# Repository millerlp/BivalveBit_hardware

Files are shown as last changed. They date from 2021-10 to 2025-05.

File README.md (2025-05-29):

# BivalveBit hardware
 Heart rate and valve gape sensor wearable for oysters and mussels. 
 This hardware is described in the publication "Monitoring bivalve behavior and physiology in the laboratory and field using open-source tools" L.P. Miller (2022) *Integrative and Comparative Biology*
 
 [https://doi.org/10.1093/icb/icac046](https://doi.org/10.1093/icb/icac046)
 
 * Based around a ATmega4808 microcontroller
 * Designed to fit inside a nominal 3/4" schedule 40 PVC plumbing pipe (<18.5mm
 inside diameter) along with an 18650 size Lithium-Ion battery cell. 
 * Provides one I2C 4-pin port for communicating with a IR heart rate sensor
 * Provides one analog 4-pin port for communicating with an analog sensor such
 as the A1395 Hall effect sensor (with SLEEP pin on the 4th wire). 
 * Writes data to a standard microSD card

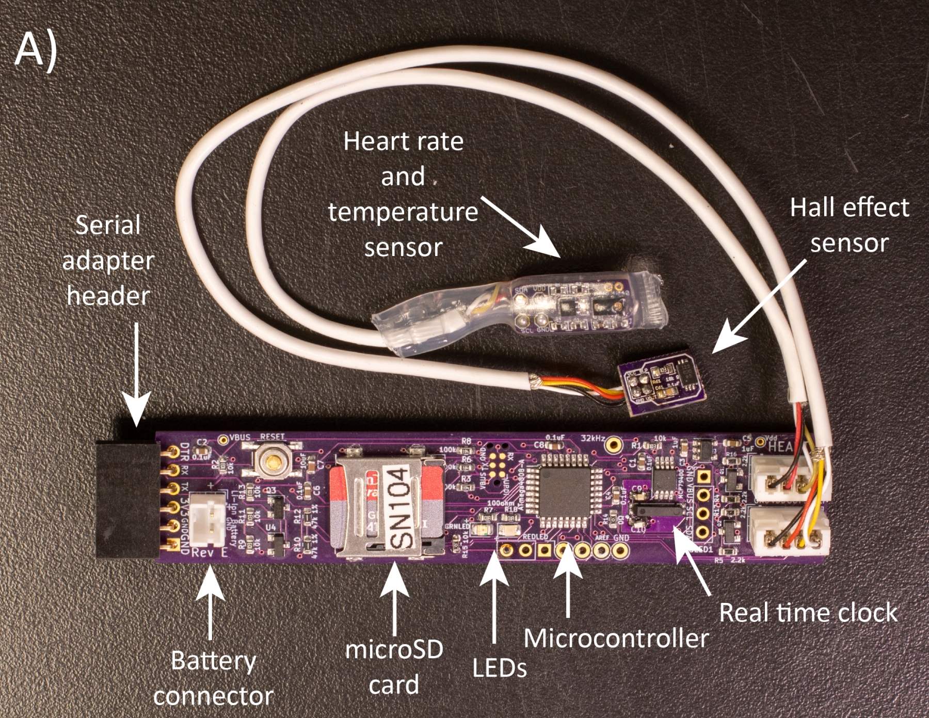
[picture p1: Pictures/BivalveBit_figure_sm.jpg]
Labeled image of the circuit board
 

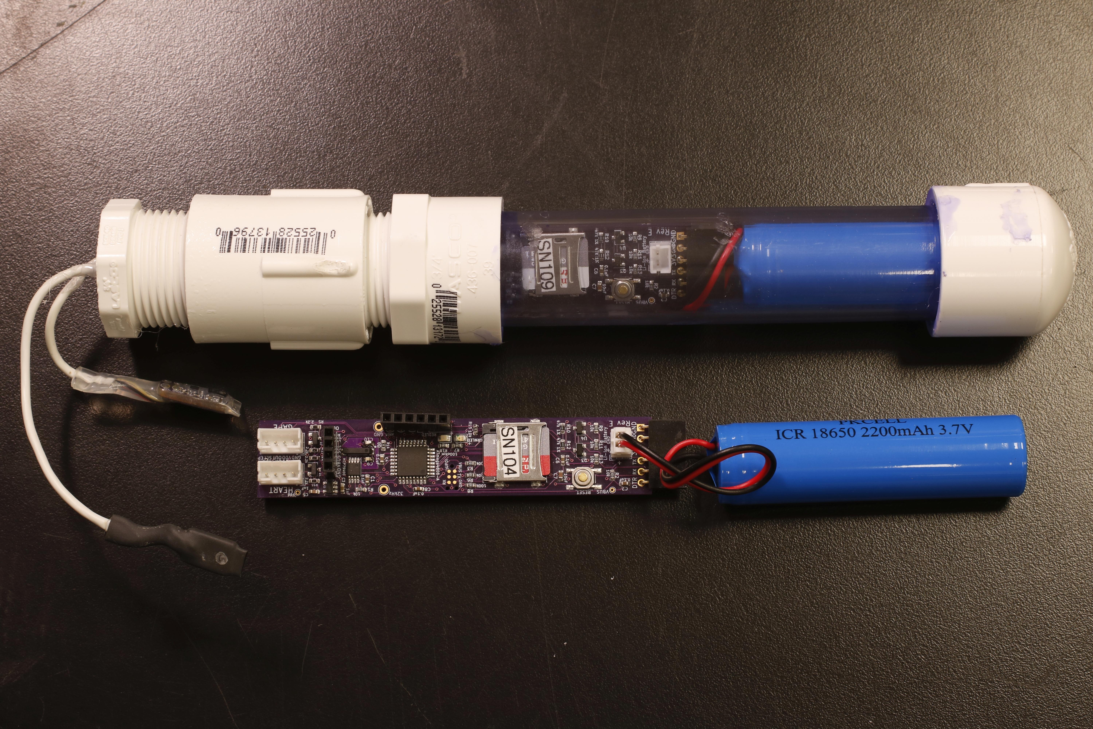
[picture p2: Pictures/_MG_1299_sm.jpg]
Data logger next to a PVC pipe housing


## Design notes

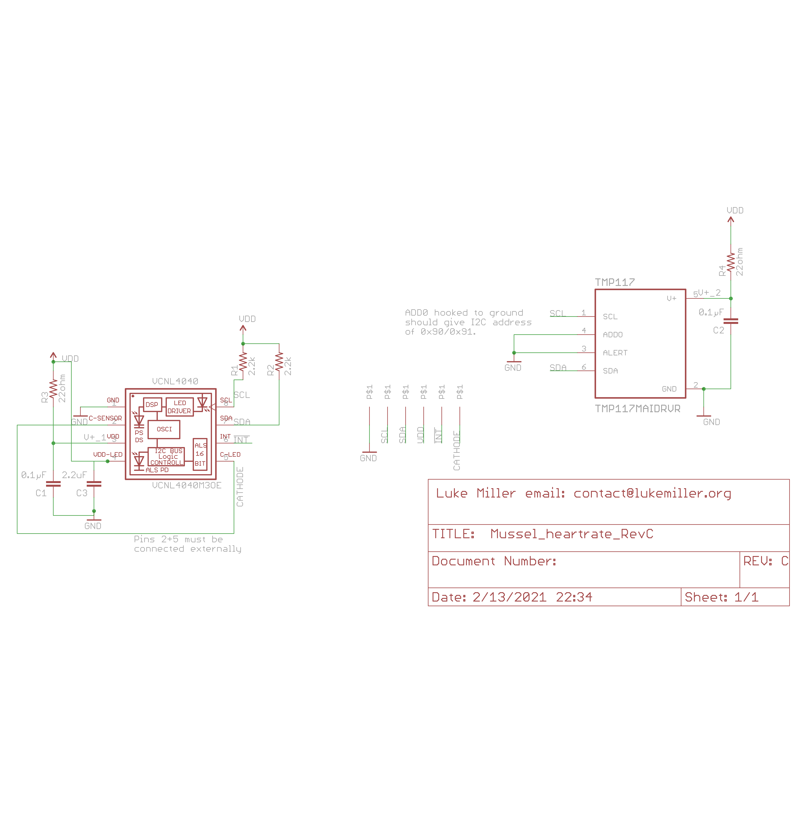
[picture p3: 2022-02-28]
Hardware/Mussel_heartrate_RevC_EAGLE/Mussel_heartrate_RevC_schematic.png

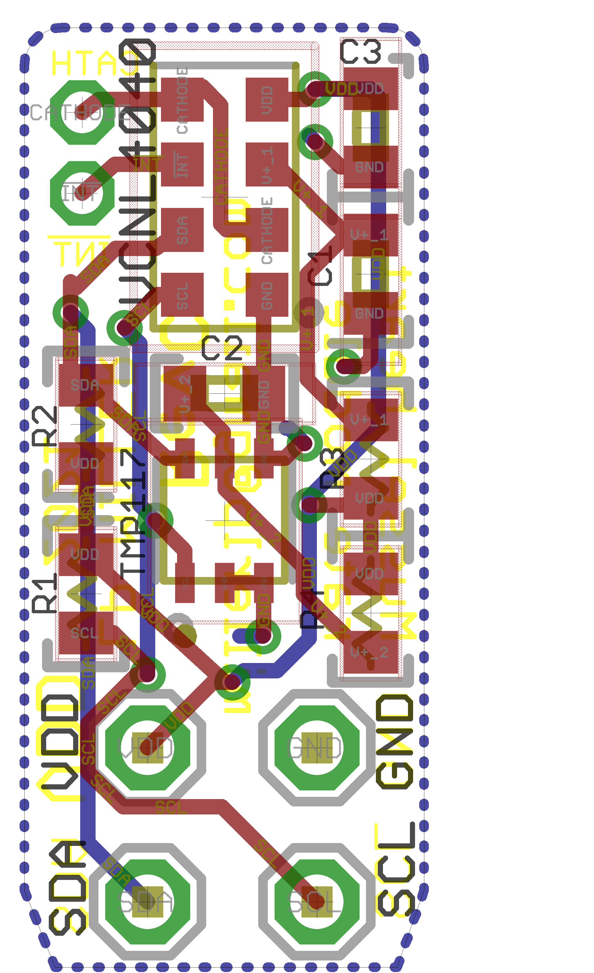
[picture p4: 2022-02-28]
Hardware/Mussel_heartrate_RevC_EAGLE/Mussel_heartrate_RevC_board.png

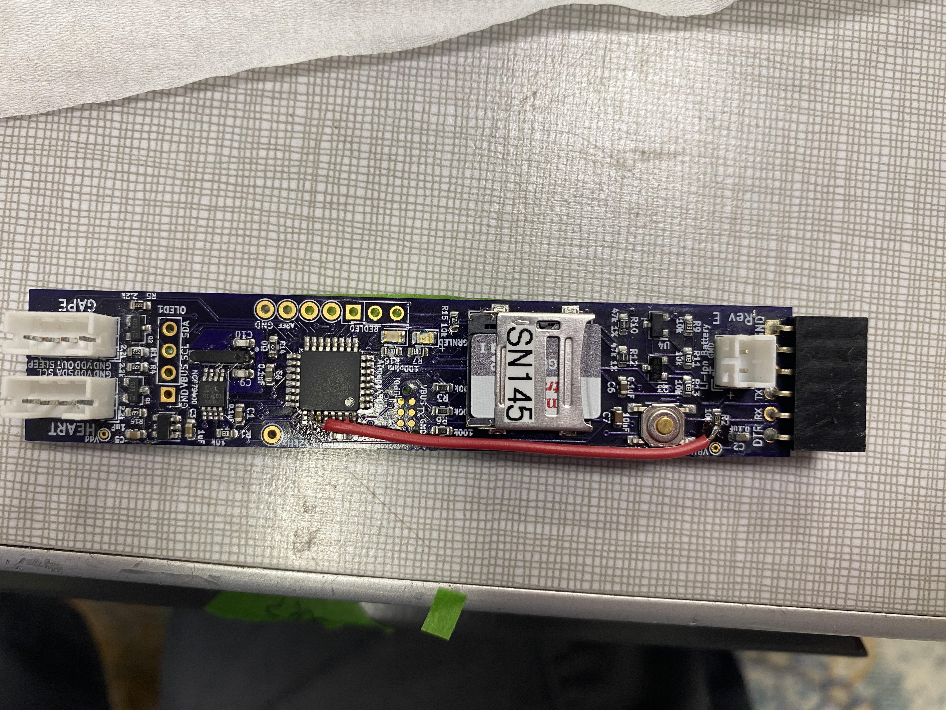
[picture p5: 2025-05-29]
Pictures/2023-08-01 10.56.35.jpg

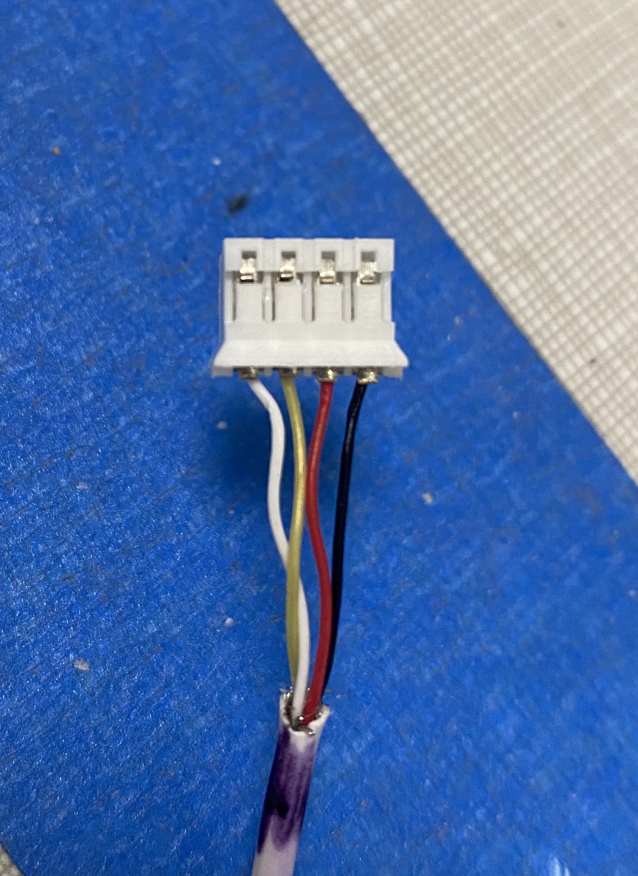
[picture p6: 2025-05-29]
Pictures/2021-09-30 13.38.30.jpg

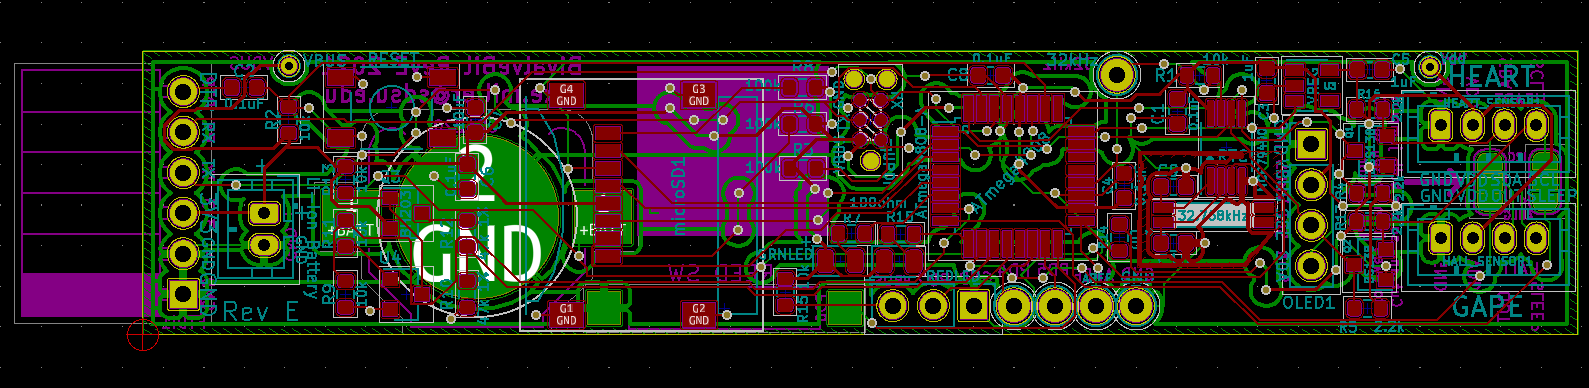
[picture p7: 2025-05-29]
Pictures/BivalveBit_layout_cropped.png

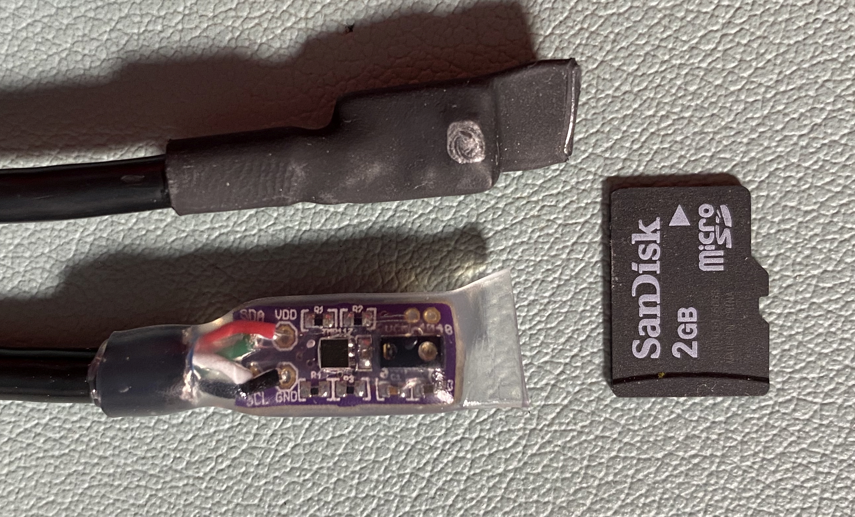
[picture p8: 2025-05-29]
Pictures/Sensors_closeup.jpg

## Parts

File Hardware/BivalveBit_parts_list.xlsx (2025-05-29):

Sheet: RevCDEF
BivalveBit RevC, RevD, RevE, RevF
Part Description | Manufacturer | Mfr. PN | Digikey PN | Quantity | Digikey $ | Extended $ | Alt. Mfr PN | Alt. Digikey PN | Digikey $
ATmega4808 32-pin TQFP package | Microchip | ATMEGA4808-AUR | 150-ATMEGA4808-AURCT-ND | 1 | $1.32 | $1.32
MCP79400 real time clock 8-MSOP | Microchip | MCP79400T-I/MS | MCP79400T-I/MSCT-ND | 1 | $0.90 | $0.90 | MCP7940NT-I/MS | MCP7940NT-I/MSCT-ND | $0.97
32.768kHz crystal 9pF ±10ppm for PCF8523 RTC | Seiko | SSPT7F-9PF10-R | 728-SSPT7F-9PF10-RCT-ND | 1 | $0.72 | $0.72
Capacitor - Crystal load 16pF ceramic 0603 1% tolerance | AVX Corp | 06035A160FAT2A | 478-06035A160FAT2ACT-ND | 2 | $0.27 | $0.54
Voltage regulator - LP5907QMFX 3.0V | Texas Inst. | LP5907QMFX-3.0Q1 | 296-40364-1-ND | 1 | $0.61 | $0.61
N-channel MOSFET - I2C level shifting, Q1,Q2 (BS138 or DMG2302U-7, Toshiba SSM3K329R,LF) | ON Semi. | BSS138 | BSS138CT-ND | 2 | $0.26 | $0.52 | DMG2302U-7 | DMG2302U-7DICT-ND | $0.40
Reed switch (optional, not used in 2022 builds) | Coto | CT10-2540-G1 | 306-1126-1-ND | 1 | $0.85 | $0.85
Capacitor 0.1uF - 0603 ceramic 25V | taiyo yuden | TMK107BJ104KA-T | 587-1245-1-ND | 5 | $0.10 | $0.50
Capacitor 1uF - 0603 ceramic X7R - for vreg | Samsung | CL10A105KB8NNNC | 1276-1860-1-ND | 2 | $0.10 | $0.20
Capacitor 10uF - 0603 ceramic - for microSD | Murata | ZRB18AR61E106ME01L | 490-10991-1-ND | 1 | $0.63 | $0.63
LED, Green 0805, 2.1V | Kingbright | APT2012CGCK | 754-1127-1-ND | 1 | $0.29 | $0.29
LED, Red 0805, 2.1V | Broadcom | HSMS-C170 | 516-1429-1-ND | 1 | $0.41 | $0.41
Resistor zero ohm, jumper 0603 | Panasonic | ERJ-3GEY0R00V | P0.0GCT-ND | 1 | $0.10 | $0.10
Resistor 100 ohm for green, red LEDs, 0603 | Yageo | RC0603FR-07100RL | 311-100HRCT-ND | 2 | $0.09 | $0.18
Resistor 2.2k ohm 5% (generic pullup) 0603 | Panasonic | ERJ-3GEYJ222V | P2.2KGCT-ND | 4 | $0.09 | $0.36
Resistor 10k 5% (generic pullup/pulldown) 0603 | Panasonic | ERJ-3GEYJ103V | P10KGCT-ND | 7 | $0.10 | $0.70
Resistor 47k 1% precision 0603 (battery voltage divider) | Panasonic | ERJ-PB3D4702V | P20473CT-ND | 2 | $0.15 | $0.30
Resistor 100k 5% (generic pullup) 0603 | Panasonic | ERJ-3GEYJ103V | P100KGCT-ND | 3 | $0.09 | $0.27
reset button - low profile | C&K | PTS525SM15SMTR2 LFS | CKN9104CT-ND | 1 | $0.27 | $0.27
MicroSD card slot hinged | Molex | 472192001 | WM6698CT-ND | 1 | $1.30 | $1.30
6-pin 0.1" pitch right angle (FTDI) | Sullins | PPPC061LGBN-RC | S5481-ND | 1 | $0.60 | $0.60
BJT NPN Transistor U4, 60V 0.1A SOT23-3 package (battery monitor) (alt FMTT619A, ZXTN25020CFHTACT-ND) |  | MMBT2484LT3G | MMBT2484LT3GOSCT-ND | 1 | $0.30 | $0.30 | MMBT6429LT1G | MMBT6429LT1GOSCT-ND | $0.21 | ZXTN25020CFHTACT-ND | 0.402
Mosfet P-FET Q3, SOT23-3 BH203,215 (battery monitor) (alt IRLML5203, Toshiba SSM3J328R,LF) |  | BSH203,215 | 1727-6216-1-ND | 1 | $0.45 | $0.45 | SSM3J328R,LF | SSM3J328RLFCT-ND | $0.39
JST PH 2-pin thru-hole for battery connection | JST | B2B-PH-K-S(LF)(SN) | 455-1704-ND | 1 | $0.45 | $0.45
CR1220 Battery holder | Keystone | 3000 | 36-3000-ND | 1 | $0.58 | $0.58
CR1220 Battery, lithium | Panasonic | CR1220 | P033-ND | 1 | $1.00 | $1.00
4 pin JST PH connector (for sensors, or hardwire) | JST | B4B-PH-K-S(LF)(SN) | 455-1706-ND | 2 | $0.24 | $0.48
4-pin JST PH receptacle housing (crimped onto wire) | JST | PHR-4 |  | 2 | $0.16 | $0.32 | 440129-4 | A100013-ND | $0.19 | TE Connectivity possibly swaps with JST PH
JST PH crimp-on connector pin, 24-30AWG | JST | SPH-002T-P0.5S |  | 8 | $0.06 | $0.48 |  | 2057-2CTC-RCT-ND |  | Possible substitute "Adam tech" that will work in JST crimper
 |  |  |  |  | Subtotal | $15.63
Sensors
Temperature sensor TMP116 (0.3C) | Texas Instruments | TMP116AIDRVR | 296-47858-1-ND | 1 | $2.89 | $2.89 | TMP117MAIDRVR | 296-51835-1-ND | $3.83
VCNL4040M30E Proximity sensor | Vishay | VCNL4040M3OE | VCNL4040M3OECT-ND | 1 | $2.40 | $2.40
2.2k ohm resistor 5% 1/16W 0402 - VCNL4040 I2C pullup |  | RC0402JR-072K2L | 311-2.2KJRCT-ND | 2 | $0.10 | $0.20
Capacitor, 2.2µF 16V 10% X7R 0402 - VCNL4040 |  | C1005X7S1A225K050BC | 445-9097-1-ND | 1 | $0.31 | $0.31
Capacitor, 0.1µF 16V 10% X7R 0402 |  | C1005X7R1C104K050BC | 445-4952-1-ND | 2 | $0.10 | $0.20
A1395 Hall effect sensor | Allegro | A1395SEHLT-T | 620-1173-1-ND | 1 | $2.00 | $2.00
Capacitor, 0603 0.1µF 16V ceramic | KEMET | C0603C104K4RACTU | 399-1096-1-ND | 1 | $0.10 | $0.10
Resistor, 0603 10 k ohm | Yageo | RC0603JR-0710KL | 311-10KGRCT-ND | 1 | $0.10 | $0.10
Magnet 0.25"diam x 0.063" thick | Radial Magnet Inc | 8195 | 469-1005-ND | 1 | $0.23 | $0.23
 |  |  |  |  | Subtotal | $24.06
18650 Li-Ion battery - Adafruit #1781 w/ JST PH connector | Adafruit | 1781 | 1528-1836-ND | 1 | $9.95 | $9.95
 |  |  |  |  | Total | $34.01
Bulk items
4-wire cable for sensors 32ga 2.0mm OD (100ft) | Tensility | 30-00218 | T1245-30-ND | 1 | $64.75
Clear heat shrink, 0.25" ID, 3:1, adhesive lined | NTE | 47-23248-CL | 2368-47-23248-CL-ND | 1 | $3.51
Alternate load capacitors
Capacitor - Crystal load 3pF ceramic 0603 0.25pF tolerance | AVX Corp | 06031A3R0CAT2A | 478-3690-1-ND | 2 | $0.21 | $0.42
Capacitor - Crystal load 6pF ceramic 0603 0.25pF tolerance | AVX Corp | 06035A6R0CAT2A | 478-10334-1-ND | 2 | $0.23 | $0.46
Capacitor - Crystal load 7pF ceramic 0603 0.25pF tolerance | AVX Corp | 06035A7R0CAT2A | 478-10337-1-ND | 2 | $0.09 | $0.18
Capacitor - Crystal load 12pF ceramic 0603 1% tolerance | AVX Corp | 06032U120FAT2A | 478-10252-1-ND | 2 | $0.34 | $0.68
Alternate parts
Allegro ALS31313 3-axis Hall sensor I2C, 500Gauss, 8-TSSOP |  | ALS31313KLEATR-500 | 620-2009-1-ND | 0 | $2.37 | $0.00
JST Hand crimper 24-30AWG side entry | JST | WC-240 | 455-1128-ND |  | $543.00

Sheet: Prototype_RevB
BivalveBit prototype
Part Description | Eagle library part | Manufacturer | Mfr. PN | Digikey PN | Quantity | Digikey $ | Extended $ | Alt. Mfr PN | Alt. Digikey PN | Digikey $
ATmega4808 32-pin TQFP package |  | Microchip | ATMEGA4808-AUR | 150-ATMEGA4808-AURCT-ND | 1 | $1.32 | $1.32
MCP79400 real time clock 8-MSOP |  | Microchip | MCP79400T-I/MS | MCP79400T-I/MSCT-ND | 1 | $0.90 | $0.90
32.768kHz crystal 9pF ±10ppm for PCF8523 RTC |  | Seiko | SSPT7F-9PF10-R | 728-SSPT7F-9PF10-RCT-ND | 1 | $0.72 | $0.72
Capacitor - Crystal load 16pF ceramic 0603 1% tolerance |  | AVX Corp | 06035A160FAT2A | 478-06035A160FAT2ACT-ND | 2 | $0.27 | $0.54
Voltage regulator - LP5907QMFX 3.0V |  | Texas Inst. | LP5907QMFX-3.0Q1 | 296-40364-1-ND | 1 | $0.61 | $0.61
N-channel MOSFET - I2C level shifting, Q1,Q2 (BS138 or DMG2302U-7, Toshiba SSM3K329R,LF) |  | ON Semi. | BSS138 | BSS138CT-ND | 2 | $0.26 | $0.52 | DMG2302U-7 | DMG2302U-7DICT-ND | $0.40
Reed switch |  | Coto | CT10-2540-G1 | 306-1126-1-ND | 1 | $0.85 | $0.85
Capacitor 0.1uF - 0603 ceramic 25V |  | taiyo yuden | TMK107BJ104KA-T | 587-1245-1-ND | 5 | $0.10 | $0.50
Capacitor 1uF - 0603 ceramic X7R - for vreg |  | Samsung | CL10A105KB8NNNC | 1276-1860-1-ND | 2 | $0.10 | $0.20
Capacitor 10uF - 0603 ceramic - for microSD |  | Murata | ZRB18AR61E106ME01L | 490-10991-1-ND | 1 | $0.63 | $0.63
LED, Green 0805, 2.1V |  | Kingbright | APT2012CGCK | 754-1127-1-ND | 1 | $0.29 | $0.29
LED, Red 0805, 2.1V |  | Broadcom | HSMS-C170 | 516-1429-1-ND | 1 | $0.41 | $0.41
Resistor zero ohm, jumper 0603 |  | Panasonic | ERJ-3GEY0R00V | P0.0GCT-ND | 1 | $0.10 | $0.10
Resistor 100 ohm for green, red LEDs, 0603 |  | Yageo | RC0603FR-07100RL | 311-100HRCT-ND | 1 | $0.09 | $0.09
Resistor 2.2k ohm 5% (generic pullup) 0603 |  | Panasonic | ERJ-3GEYJ222V | P2.2KGCT-ND | 4 | $0.09 | $0.36
Resistor 10k 5% (generic pullup/pulldown) 0603 |  | Panasonic | ERJ-3GEYJ103V | P10KGCT-ND | 7 | $0.10 | $0.70
Resistor 47k 1% precision 0603 (battery voltage divider) |  | Panasonic | ERJ-PB3D4702V | P20473CT-ND | 2 | $0.15 | $0.30
Resistor 100k 5% (generic pullup) 0603 |  | Panasonic | ERJ-3GEYJ103V | P100KGCT-ND | 3 | $0.09 | $0.27
reset button - low profile |  | C&K | PTS525SM15SMTR2 LFS | CKN9104CT-ND | 1 | $0.27 | $0.27
MicroSD card slot hinged |  | Molex | 472192001 | WM6698CT-ND | 1 | $1.30 | $1.30
6-pin 0.1" pitch right angle (FTDI) |  | Sullins | PPPC061LGBN-RC | S5481-ND | 1 | $0.60 | $0.60
4 pin JST PH connector (for sensors, or hardwire?) |  | JST | B4B-PH-K-S(LF)(SN) | 455-1706-ND | 2 | $0.24 | $0.48
BJT NPN Transistor U4, 60V 0.1A SOT23-3 package (battery monitor) (alt FMTT619A) |  |  | MMBT2484LT3G | MMBT2484LT3GOSCT-ND | 1 | $0.30 | $0.30
Mosfet P-FET Q3, SOT23-3 BH203,215 (battery monitor) (alt IRLML5203, Toshiba SSM3J328R,LF) |  |  | BSH203,215 | 1727-6216-1-ND | 1 | $0.45 | $0.45 | SSM3J328R,LF | SSM3J328RLFCT-ND | $0.39
JST PH 2-pin surface mount for battery connection (right angle out of stock) |  | JST | B2B-PH-SM4-TB(LF)(SN) | 455-1734-1-ND | 1 | $0.45 | $0.45
CR1220 Battery holder |  | Keystone | 3000 | 36-3000-ND | 1 | $0.58 | $0.58
CR1220 Battery, lithium |  | Panasonic | CR1220 | P033-ND | 1 | $1.00 | $1.00
 |  |  |  |  |  | Subtotal | $14.74
Sensors
Temperature sensor TMP116 (0.3C) |  | Texas Instruments | TMP116AIDRVR | 296-47858-1-ND | 1 | $2.89 | $2.89
VCNL4040M30E Proximity sensor |  | Vishay | VCNL4040M3OE | VCNL4040M3OECT-ND | 1 | $2.40 | $2.40
2.2k ohm resistor 5% 1/16W 0402 - VCNL4040 I2C pullup |  |  | RC0402JR-072K2L | 311-2.2KJRCT-ND | 2 | $0.10 | $0.20
Capacitor, 2.2µF 16V 10% X7R 0402 - VCNL4040 |  |  | C1005X7S1A225K050BC | 445-9097-1-ND | 1 | $0.31 | $0.31
Capacitor, 0.1µF 16V 10% X7R 0402 |  |  | C1005X7R1C104K050BC | 445-4952-1-ND | 2 | $0.10 | $0.20
A1395 Hall effect sensor |  | Allegro | A1395SEHLT-T | 620-1173-1-ND | 1 | $2.00 | $2.00
Capacitor, 0603 0.1µF 16V ceramic |  | KEMET | C0603C104K4RACTU | 399-1096-1-ND | 1 | $0.10 | $0.10
Resistor, 0603 10 k ohm |  | Yageo | RC0603JR-0710KL | 311-10KGRCT-ND | 1 | $0.10 | $0.10
Magnet 0.25"diam x 0.063" thick |  | Radial Magnet Inc | 8195 | 469-1005-ND | 1 | $0.23 | $0.23
4-wire cable for sensors
 |  |  |  |  |  | Total | $20.39
Alternate load capacitors
Capacitor - Crystal load 3pF ceramic 0603 0.25pF tolerance |  | AVX Corp | 06031A3R0CAT2A | 478-3690-1-ND | 2 | $0.21 | $0.42
Capacitor - Crystal load 6pF ceramic 0603 0.25pF tolerance |  | AVX Corp | 06035A6R0CAT2A | 478-10334-1-ND | 2 | $0.23 | $0.46
Capacitor - Crystal load 7pF ceramic 0603 0.25pF tolerance |  | AVX Corp | 06035A7R0CAT2A | 478-10337-1-ND | 2 | $0.09 | $0.18
Capacitor - Crystal load 12pF ceramic 0603 1% tolerance |  | AVX Corp | 06032U120FAT2A | 478-10252-1-ND | 2 | $0.34 | $0.68
Alternate parts - out of stock?
PCF8523 real time clock 14-TSSOP |  | NXP | PCF8523TS/1,118 | 568-6649-1-ND | 0 | $1.41 | $0.00

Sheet: Crystal_specs
ATmega4809/4808 specify minimum crystal load of 7.5pF, maximum 12.5pF. See table 32-15 in datasheet pg 469
 | Internal load | Parasitic | External 1 | External 2
 | Cload | Cpara | Cex1 | Cex2 | Total load
 | 5.5 | 0.5 | 0 | 0 | 3
 | 5.5 | 0.5 | 10 | 13 | 8.685714286
 | 5.5 | 0.5 | 10 | 13 | 8.685714286
 | 5.5 | 0.5 | 12 | 12 | 9
 | 5.5 | 0.5 | 16 | 16 | 11
 | 5.5 | 0.5 | 22 | 22 | 14
MCP79400 real time clock specifies crystal load of 6-9pf, Seiko SSPT7F-9PF10-R is 9pF load
 | Cload | Cpara (stray) | CX1 | CX2 | Cosc | Total load | C1,C2 alternate calculation
 | 9 | 0.5 | 1 | 1 | 3 | 1 | 17
 | 9 | 0.5 | 16 | 16 | 3 | 8.5 | 17
 | 9 | 0.5 | 14 | 14 | 3 | 9 | 17
 | 9 | 1 | 13 | 13 | 3 | 9 | 16
 | 9 | 1.5 | 12 | 12 | 3 | 9 | 15
 | 9 | 3 | 9 | 9 | 3 | 9 | 12
 | 9 | 4 | 7 | 7 | 3 | 9 | 10
 | 9 | 5 | 5 | 5 | 3 | 9 | 8
 | 9 | 6 | 3 | 3 | 3 | 9 | 6

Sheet: RTC_prescaler_calcs
kHz | prescaler | cycles/sec | Period | Interrupt/sec
32768 | 32 | 1024 | 512 | 2
32768 | 32 | 1024 | 256 | 4
32768 | 32 | 1024 | 128 | 8
32768 | 32 | 1024 | 64 | 16
32768 | 32 | 1024 | 32 | 32
32768 | 4 | 8192 | 4096 | 2
32768 | 4 | 8192 | 2048 | 4
32768 | 4 | 8192 | 1024 | 8
32768 | 4 | 8192 | 512 | 16
32768 | 4 | 8192 | 256 | 32
32768 | 4 | 8192 | 128 | 64
32768 | 4 | 8192 | 64 | 128
32768 | 4 | 8192 | 32 | 256
32768 | 4 | 8192 | 16 | 512

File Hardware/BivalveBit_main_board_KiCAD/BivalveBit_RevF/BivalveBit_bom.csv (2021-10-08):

Id | Designator | Package | Quantity | Designation | Supplier and ref
1 | TP2,TP1 | TestPoint_THTPad_D1.0mm_Drill0.5mm | 2 | TestPoint_Probe
2 | RTC_BATT1 | BatteryHolder_Keystone_3000_1x12mm | 1 | Battery_Cell
3 | JP2,JP1 | SolderJumper-3_P1.3mm_Bridged12_RoundedPad1.0x1.5mm | 2 | SolderJumper_3_Bridged12
4 | HEART_SENSOR1,HALL_SENSOR1 | JST_PH_B4B-PH-K_1x04_P2.00mm_Vertical | 2 | Conn_01x04_Male
5 | R17,R16,R5,R4 | R_0603_1608Metric | 4 | 2.2k
6 | U4 | SOT-23 | 1 | BJT_NPN
7 | U3 | SOT-23-5 | 1 | LP5907MFX-3.0
8 | U2 | TQFP-32_7x7mm_P0.8mm | 1 | ATmega4808-A
9 | SW2 | SW_SPST_REED_CT10-XXXX-G1 | 1 | SW_Reed
10 | RESET1 | SW_PTS525SM15SMTR2LFS | 1 | PTS525SM15SMTR2LFS
11 | R15,R13,R11,R9,R2,R1 | R_0603_1608Metric | 6 | 10k
12 | R14 | R_0603_1608Metric | 1 | 0Ω
13 | R12,R10 | R_0603_1608Metric | 2 | 47k 1%
14 | R8,R6,R3 | R_0603_1608Metric | 3 | 100k
15 | R7,R18 | R_0603_1608Metric | 2 | 100ohm
16 | Q3 | SOT-23 | 1 | P-FET
17 | Q2,Q1 | SOT-23 | 2 | BSS138
18 | PROGRAM_HEADER1 | Tag-Connect_TC2030-IDC-NL_2x03_P1.27mm_Vertical | 1 | TC2030-IDC-NL-UPDI
19 | PRIMARY_BATTERY1 | JST_PH_B2B-PH-K_1x02_P2.00mm_Vertical | 1 | Conn_01x02
20 | OLED1 | PinHeader_1x04_P2.54mm_Vertical | 1 | Conn_01x04
21 | microSD1 | MOLEX_47219-2001 | 1 | 47219-2001
22 | J7,J5,J4,J8,J2 | Pin_D1.0mm_L10.0mm | 5 | Conn_01x01_Male
23 | J6 | PinHeader_1x03_P2.54mm_Vertical | 1 | Conn_01x03_Male
24 | FTDI1 | PinSocket_1x06_P2.54mm_Horizontal | 1 | Conn_01x06
25 | D1 | LED_0805_2012Metric | 1 | GRNLED
26 | Crystal_32.768kHz1 | OSC_SSP-T7-F | 1 | SSP-T7-F
27 | C8,C6,C4,C2,C1 | C_0603_1608Metric | 5 | 0.1uF
28 | C7 | C_0603_1608Metric | 1 | 10uF
29 | C5,C3 | C_0603_1608Metric | 2 | 1uF
30 | C9,C10 | C_0603_1608Metric | 2 | 4-16pF
31 | RTC1 | MSOP-8_3x3mm_P0.65mm | 1 | MCP79400
32 | D2 | LED_0805_2012Metric | 1 | REDLED

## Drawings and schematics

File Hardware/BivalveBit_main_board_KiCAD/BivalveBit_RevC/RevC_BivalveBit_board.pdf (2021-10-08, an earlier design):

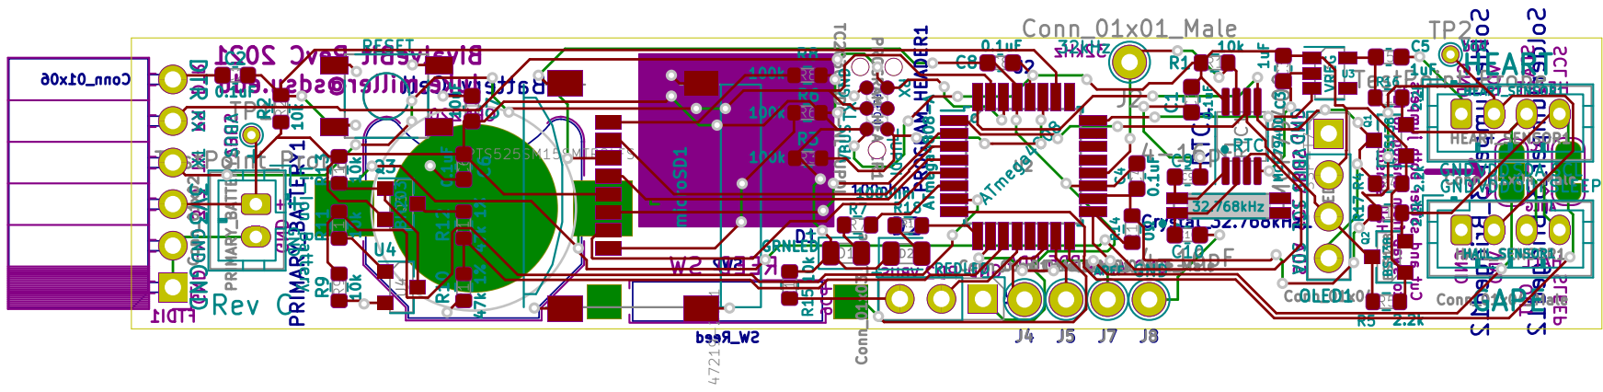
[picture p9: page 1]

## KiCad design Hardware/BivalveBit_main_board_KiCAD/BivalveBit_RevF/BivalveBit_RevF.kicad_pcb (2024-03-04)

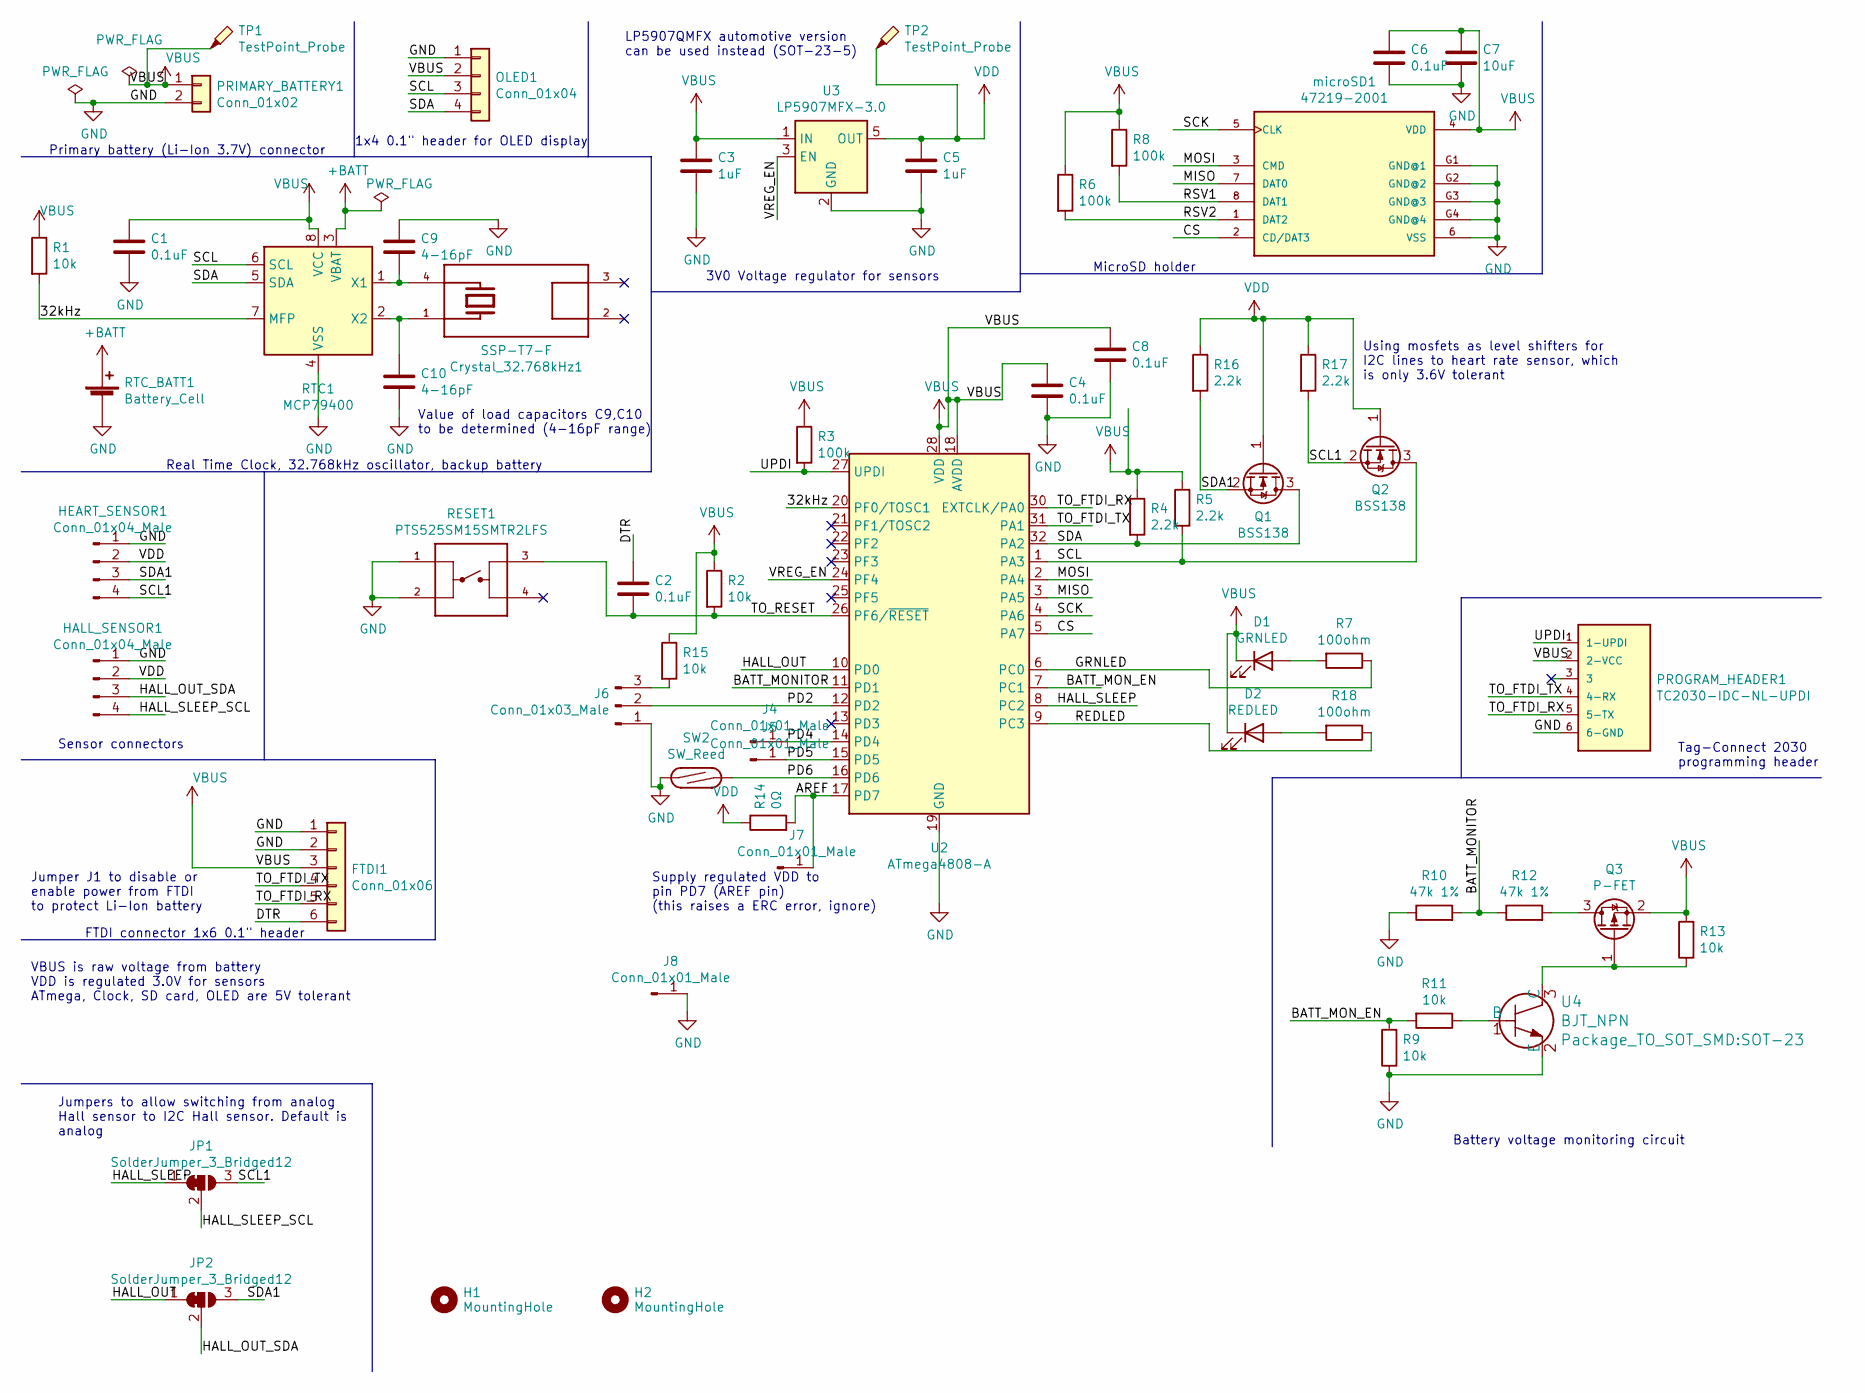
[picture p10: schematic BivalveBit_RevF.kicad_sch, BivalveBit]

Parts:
C1, C2, C4, C6, C8: 0.1uF; C_0603_1608Metric
C3, C5: 1uF; C_0603_1608Metric
C7: 10uF; C_0603_1608Metric
C9, C10: 4-16pF; C_0603_1608Metric
Crystal_32.768kHz1: SSP-T7-F; OSC_SSP-T7-F; PARTREV N/A
D1: GRNLED; LED_0805_2012Metric
D2: REDLED; LED_0805_2012Metric
FTDI1: Conn_01x06; PinSocket_1x06_P2.54mm_Horizontal
H1, H2: MountingHole; MountingHole_3.2mm_M3
HALL_SENSOR1: Conn_01x04_Male; JST_PH_B4B-PH-K_1x04_P2.00mm_Vertical
HEART_SENSOR1: Conn_01x04_Male; JST_PH_B4B-PH-K_1x04_P2.00mm_Vertical
J4, J5, J7, J8: Conn_01x01_Male; Pin_D1.0mm_L10.0mm
J6: Conn_01x03_Male; PinHeader_1x03_P2.54mm_Vertical
JP1, JP2: SolderJumper_3_Bridged12; SolderJumper-3_P1.3mm_Bridged12_RoundedPad1.0x1.5mm
OLED1: Conn_01x04; PinHeader_1x04_P2.54mm_Vertical
PRIMARY_BATTERY1: Conn_01x02; JST_PH_B2B-PH-K_1x02_P2.00mm_Vertical
PROGRAM_HEADER1: TC2030-IDC-NL-UPDI; Tag-Connect_TC2030-IDC-NL_2x03_P1.27mm_Vertical; PARTREV MS
Q1, Q2: BSS138; SOT-23
Q3: P-FET; SOT-23
R1, R2, R9, R11, R13, R15: 10k; R_0603_1608Metric
R3, R6, R8: 100k; R_0603_1608Metric
R4, R5, R16, R17: 2.2k; R_0603_1608Metric
R7, R18: 100ohm; R_0603_1608Metric
R10, R12: 47k 1%; R_0603_1608Metric
R14: 0Ω; R_0603_1608Metric
RESET1: PTS525SM15SMTR2LFS; SW_PTS525SM15SMTR2LFS; PARTREV NA
RTC1: MCP79400; MSOP-8_3x3mm_P0.65mm
RTC_BATT1: Battery_Cell; BatteryHolder_Keystone_3000_1x12mm
SW2: SW_Reed; SW_SPST_REED_CT10-XXXX-G1
TP1, TP2: TestPoint_Probe; TestPoint_THTPad_D1.0mm_Drill0.5mm
U2: ATmega4808-A; TQFP-32_7x7mm_P0.8mm
U3: LP5907MFX-3.0; SOT-23-5
U4: BJT_NPN; SOT-23
microSD1: 47219-2001; MOLEX_47219-2001; Digikey WM6698CT-ND

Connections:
+BATT: RTC1.3 (VBAT), RTC_BATT1.1 (+)
/32kHz: R1.2, RTC1.7 (MFP), U2.20 (PF0/TOSC1)
/AREF: J7.1, R14.2, U2.17 (PD7)
/BATT_MONITOR: R10.2, R12.1, U2.11 (PD1)
/BATT_MON_EN: R9.2, R11.2, U2.7 (PC1)
/CS: U2.5 (PA7), microSD1.2 (CD/DAT3)
/DTR: C2.1, FTDI1.6
/GRNLED: R7.1, U2.6 (PC0)
/HALL_OUT: JP2.1 (A), U2.10 (PD0)
/HALL_OUT_SDA: HALL_SENSOR1.3, JP2.2 (C)
/HALL_SLEEP: JP1.1 (A), U2.8 (PC2)
/HALL_SLEEP_SCL: HALL_SENSOR1.4, JP1.2 (C)
/MISO: U2.3 (PA5), microSD1.7 (DAT0)
/MOSI: U2.2 (PA4), microSD1.3 (CMD)
/PD2: J6.2, U2.12 (PD2)
/PD4: J4.1, U2.14 (PD4)
/PD5: J5.1, U2.15 (PD5)
/PD6: SW2.2, U2.16 (PD6)
/REDLED: R18.1, U2.9 (PC3)
/RSV1: R8.2, microSD1.8 (DAT1)
/RSV2: R6.2, microSD1.1 (DAT2)
/SCK: U2.4 (PA6), microSD1.5 (CLK)
/SCL: OLED1.3, Q2.3 (D), R5.2, RTC1.6 (SCL), U2.1 (PA3)
/SCL1: HEART_SENSOR1.4, JP1.3 (B), Q2.2 (S), R17.2
/SDA: OLED1.4, Q1.3 (D), R4.2, RTC1.5 (SDA), U2.32 (PA2)
/SDA1: HEART_SENSOR1.3, JP2.3 (B), Q1.2 (S), R16.2
/TO_FTDI_RX: FTDI1.5, PROGRAM_HEADER1.5 (5-TX), U2.30 (EXTCLK/PA0)
/TO_FTDI_TX: FTDI1.4, PROGRAM_HEADER1.4 (4-RX), U2.31 (PA1)
/TO_RESET: C2.2, R2.2, RESET1.3, U2.26 (PF6/~RESET)
/UPDI: PROGRAM_HEADER1.1 (1-UPDI), R3.2, U2.27 (UPDI)
/VREG_EN: U2.24 (PF4), U3.3 (EN)
GND: C1.2, C3.2, C4.2, C5.2, C6.2, C7.2, C8.2, C9.1, C10.2, FTDI1.1, FTDI1.2, HALL_SENSOR1.1, HEART_SENSOR1.1, J6.1, J8.1, OLED1.1, PRIMARY_BATTERY1.2, PROGRAM_HEADER1.6 (6-GND), R9.1, R10.1, RESET1.1, RESET1.2, RTC1.4 (VSS), RTC_BATT1.2 (-), SW2.1, U2.19 (GND), U2.29 (GND), U3.2 (GND), U4.2 (E), microSD1.6 (VSS), microSD1.G1 (GND@1), microSD1.G2 (GND@2), microSD1.G3 (GND@3), microSD1.G4 (GND@4)
unnamed: D1.2 (A), R7.2
unnamed: D2.2 (A), R18.2
unnamed: J6.3, R15.2
unnamed: Q3.3 (D), R12.2
unnamed: Q3.1 (G), R13.1, U4.3 (C)
unnamed: C9.2, Crystal_32.768kHz1.4, RTC1.1 (X1)
unnamed: C10.1, Crystal_32.768kHz1.1, RTC1.2 (X2)
unnamed: R11.1, U4.1 (B)
VBUS: C1.1, C3.1, C4.1, C6.1, C7.1, C8.1, D1.1 (K), D2.1 (K), FTDI1.3, OLED1.2, PRIMARY_BATTERY1.1, PROGRAM_HEADER1.2 (2-VCC), Q3.2 (S), R1.1, R2.1, R3.1, R4.1, R5.1, R6.1, R8.1, R13.2, R15.1, RTC1.8 (VCC), TP1.1, U2.18 (AVDD), U2.28 (VDD), U3.1 (IN), microSD1.4 (VDD)
VDD: C5.1, HALL_SENSOR1.2, HEART_SENSOR1.2, Q1.1 (G), Q2.1 (G), R14.1, R16.1, R17.1, TP2.1, U3.5 (OUT)

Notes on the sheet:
Primary battery (Li-Ion 3.7V) connector
Battery voltage monitoring circuit
Using mosfets as level shifters for I2C lines to heart rate sensor, which is only 3.6V tolerant
Jumpers to allow switching from analog Hall sensor to I2C Hall sensor. Default is analog
FTDI connector 1x6 0.1" header
Sensor connectors
1x4 0.1" header for OLED display
Real Time Clock, 32.768kHz oscillator, backup battery
Supply regulated VDD to pin PD7 (AREF pin) (this raises a ERC error, ignore)
Value of load capacitors C9,C10 to be determined (4-16pF range)
LP5907QMFX automotive version can be used instead (SOT-23-5)
Jumper J1 to disable or enable power from FTDI to protect Li-Ion battery
3V0 Voltage regulator for sensors
VBUS is raw voltage from battery VDD is regulated 3.0V for sensors ATmega, Clock, SD card, OLED are 5V tolerant
MicroSD holder
Tag-Connect 2030 programming header

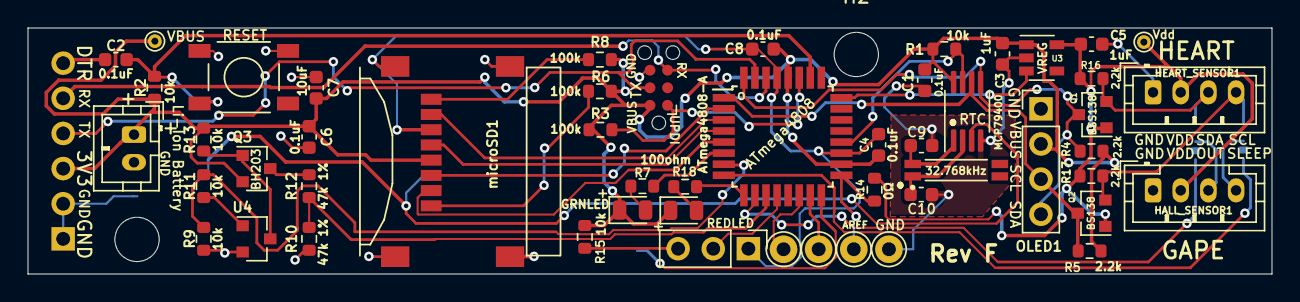
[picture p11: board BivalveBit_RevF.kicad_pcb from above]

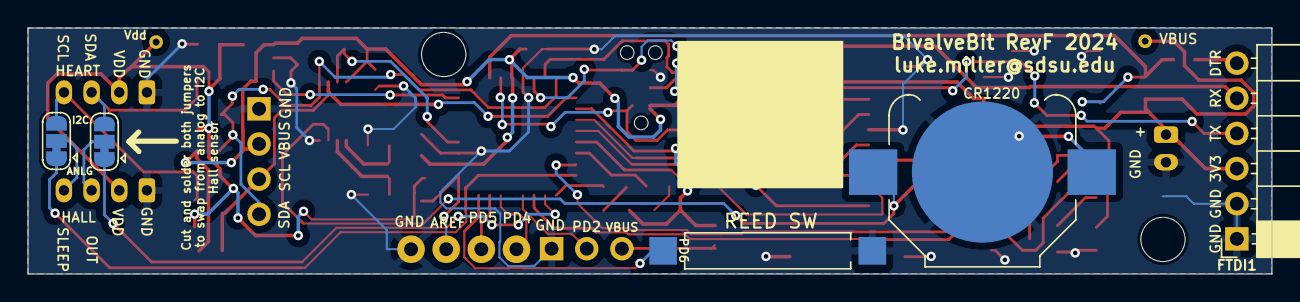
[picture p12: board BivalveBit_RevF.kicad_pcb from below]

Board: 2 copper layers, 89.9 x 17.8 mm, 59 parts (5 on the bottom side), 42 nets.

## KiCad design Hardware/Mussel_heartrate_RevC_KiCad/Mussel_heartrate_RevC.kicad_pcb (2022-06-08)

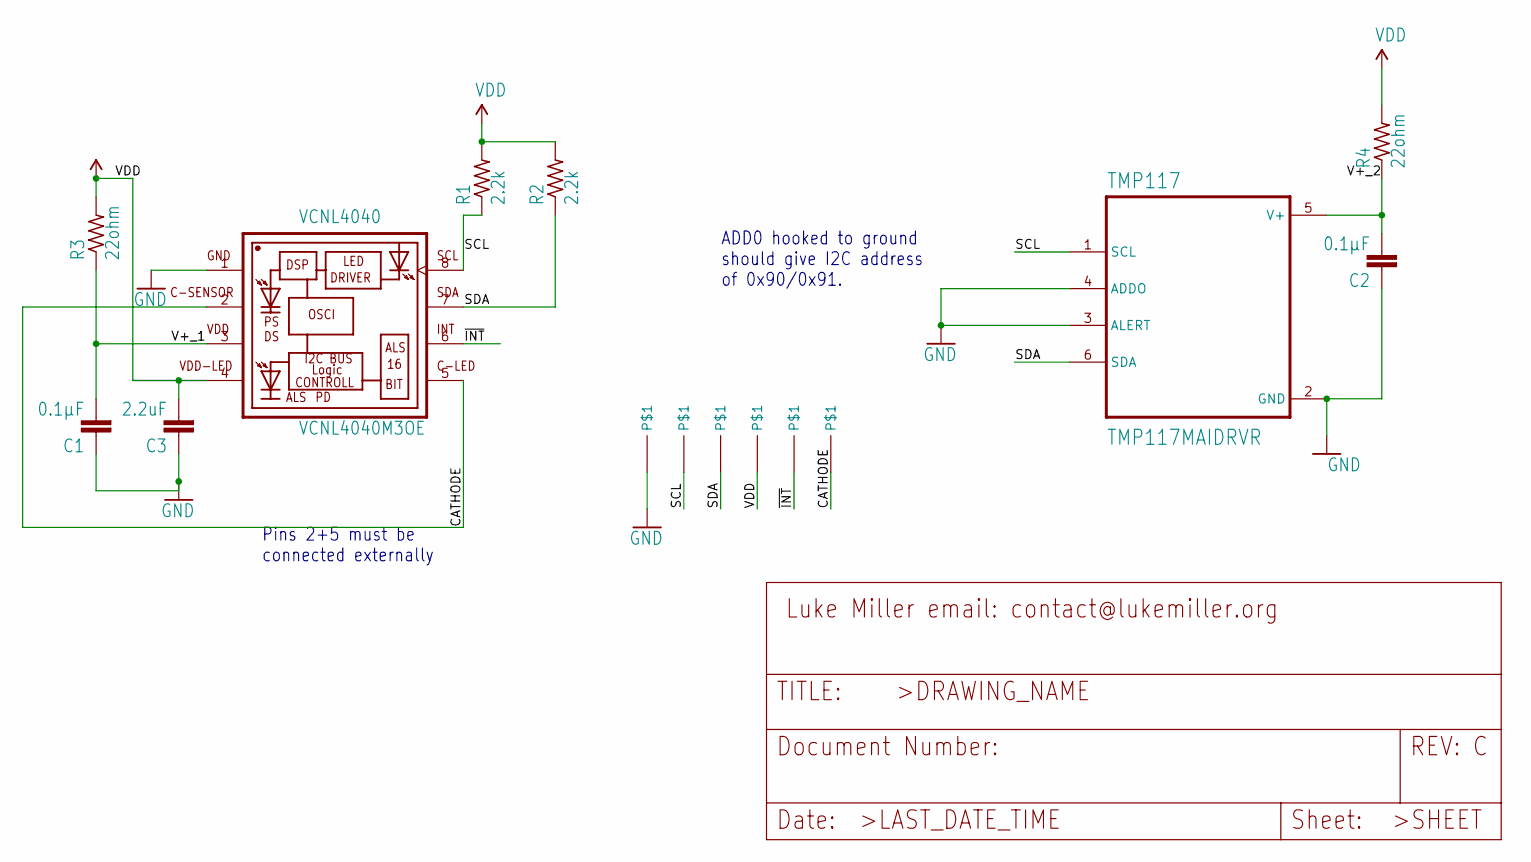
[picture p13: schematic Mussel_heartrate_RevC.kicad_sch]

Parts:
/~{INT}1: PINHD-1X10.7MM_DRILL; 1X01_SMALL_0.7
C1, C2: 0.1µF; C0402
C3: 2.2uF; C0402
CATHODE1: PINHD-1X10.7MM_DRILL; 1X01_SMALL_0.7
GND1: PINHD-1X1SMALL; 1X01_SMALL_HEADER_PIN_D0.9MM_W1.4MM
R1, R2: 2.2k; R0402
R3, R4: 22ohm; R0402
SCL1: PINHD-1X1SMALL; 1X01_SMALL_HEADER_PIN_D0.9MM_W1.4MM
SDA1: PINHD-1X1SMALL; 1X01_SMALL_HEADER_PIN_D0.9MM_W1.4MM
TMP117: TMP117MAIDRVR; SON65P200X200X80-7N
VCNL4040: VCNL4040M3OE; VISHAY_VCNL4040_4X2X1.1
VDD1: PINHD-1X1SMALL; 1X01_SMALL_HEADER_PIN_D0.9MM_W1.4MM

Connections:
/CATHODE: CATHODE1.P$1, VCNL4040.2 (C-SENSOR), VCNL4040.5 (C-LED)
/SCL: R1.1, SCL1.1, TMP117.1 (SCL), VCNL4040.8 (SCL)
/SDA: R2.1, SDA1.1, TMP117.6 (SDA), VCNL4040.7 (SDA)
/V+_1: C1.2, R3.1, VCNL4040.3 (VDD)
/V+_2: C2.2, R4.1, TMP117.5 (V+)
/~INT: /~{INT}1.P$1, VCNL4040.6 (INT)
GND: C1.1, C2.1, C3.1, GND1.1, TMP117.2 (GND), TMP117.3 (ALERT), TMP117.4 (ADDO), VCNL4040.1 (GND)
VCC: C3.2, R1.2, R2.2, R3.2, R4.2, VCNL4040.4 (VDD-LED), VDD1.1

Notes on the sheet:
ADD0 hooked to ground should give I2C address of 0x90/0x91.
Pins 2+5 must be connected externally

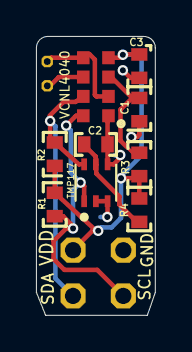
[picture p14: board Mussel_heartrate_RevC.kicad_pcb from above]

Board: 2 copper layers, 6.6 x 15.5 mm, 15 parts (0 on the bottom side), 8 nets.

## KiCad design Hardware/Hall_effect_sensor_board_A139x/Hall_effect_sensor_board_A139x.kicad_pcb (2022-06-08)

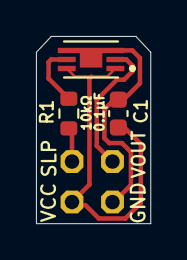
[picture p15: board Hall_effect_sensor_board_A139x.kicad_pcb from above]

Board: 2 copper layers, 6.4 x 10.4 mm, 4 parts (0 on the bottom side), 5 nets.

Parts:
C1: 0.1µF; C_0603_1608Metric
HALL1_HEADER1: PINHD-2X21.5MM_SILK; 2X2_2.25MM
R1: 10kΩ; R_0603_1608Metric
U1: A1395SEHLT-T; SENSOR_A1395SEHLT-T

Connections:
/HALL1_GND: C1.2, HALL1_HEADER1.P$1 (1), U1.3 (GND), U1.4 (GND)
/HALL1_VCC: C1.1, HALL1_HEADER1.P$2 (2), U1.1 (VCC), U1.6 (VREF)
/HALL1_VOUT: HALL1_HEADER1.P$3 (3), U1.2 (OUT)
/HALL1_~SLEEP_IN: HALL1_HEADER1.P$4 (4), R1.1
/~SLEEP1: R1.2, U1.5 (~SLEEP)

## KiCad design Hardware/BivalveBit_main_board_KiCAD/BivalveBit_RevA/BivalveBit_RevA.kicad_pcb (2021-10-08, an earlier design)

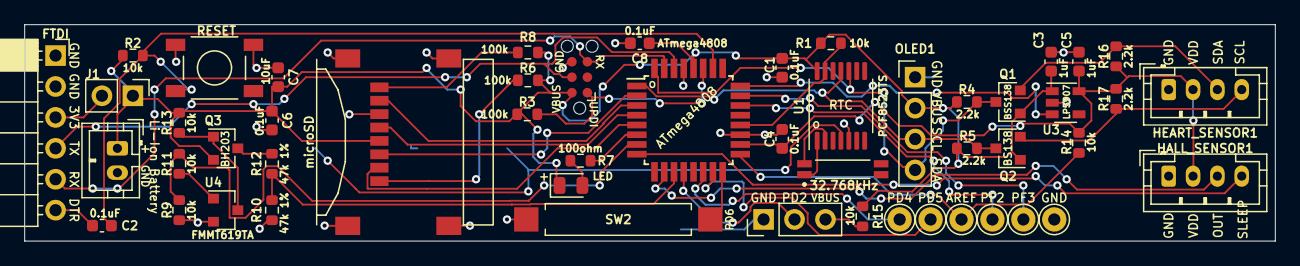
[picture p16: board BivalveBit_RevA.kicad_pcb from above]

Board: 2 copper layers, 102.7 x 17.8 mm, 52 parts (1 on the bottom side), 41 nets.

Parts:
32.768kHz: SSP-T7-F; OSC_SSP-T7-F
C1, C2, C4, C6, C8: 0.1uF; C_0603_1608Metric
C3, C5: 1uF; C_0603_1608Metric
C7: 10uF; C_0603_1608Metric
D1: LED; LED_0805_2012Metric
FTDI: Conn_01x06; PinSocket_1x06_P2.54mm_Horizontal
HALL_SENSOR1: Conn_01x04_Male; JST_PH_B4B-PH-K_1x04_P2.00mm_Vertical
HEART_SENSOR1: Conn_01x04_Male; JST_PH_B4B-PH-K_1x04_P2.00mm_Vertical
J1: Conn_01x02_Male; PinHeader_1x02_P2.54mm_Vertical
J2, J3, J4, J5, J7, J8: Conn_01x01_Male; Pin_D1.0mm_L10.0mm
J6: Conn_01x03_Male; PinHeader_1x03_P2.54mm_Vertical
OLED1: Conn_01x04; PinHeader_1x04_P2.54mm_Vertical
PRIMARY_BATTERY1: Conn_01x02; JST_PH_B2B-PH-K_1x02_P2.00mm_Vertical
PROGRAM_HEADER1: TC2030-IDC-NL-UPDI; Tag-Connect_TC2030-IDC-NL_2x03_P1.27mm_Vertical
Q1, Q2: BSS138; SOT-23
Q3: IRLML5203 or BH203,215; SOT-23
R1, R2, R9, R11, R13, R14, R15: 10k; R_0603_1608Metric
R3, R6, R8: 100k; R_0603_1608Metric
R4, R5, R16, R17: 2.2k; R_0603_1608Metric
R7: 100ohm; R_0603_1608Metric
R10, R12: 47k 1%; R_0603_1608Metric
RESET: PTS525SM15SMTR2LFS; SW_PTS525SM15SMTR2LFS
RTC_BATT1: Battery_Cell; BatteryHolder_Keystone_3000_1x12mm_small_pad
SW2: SW_Reed; SW_SPST_REED_CT10-XXXX-G1
U1: PCF8523TS; TSSOP-14_4.4x5mm_P0.65mm
U2: ATmega4808; TQFP-32_7x7mm_P0.8mm
U3: LP5907; SOT-23-5
U4: FMMT619TA; SOT-23
microSD: 47219-2001; MOLEX_47219-2001

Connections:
+BATT: RTC_BATT1.1, U1.4
/3V3_FTDI: FTDI.3, J1.2
/32kHz: R1.2, U1.13, U2.20
/AREF: J7.1, R14.2, U2.17
/BATT_MONITOR: R10.2, R12.1, U2.11
/BATT_MON_EN: R9.2, R11.2, U2.7
/CS: U2.5, microSD.2
/DTR: C2.1, FTDI.6
/HALL_OUT: HALL_SENSOR1.3, U2.10
/HALL_SLEEP: HALL_SENSOR1.4, U2.8
/LED: R7.1, U2.6
/MISO: U2.3, microSD.7
/MOSI: U2.2, microSD.3
/PD2: J6.2, U2.12
/PD4: J4.1, U2.14
/PD5: J5.1, U2.15
/PD6: SW2.2, U2.16
/PF2: J2.1, U2.22
/PF3: J3.1, U2.23
/RSV1: R8.2, microSD.8
/RSV2: R6.2, microSD.1
/SCK: U2.4, microSD.5
/SCL: OLED1.3, Q2.3, R5.2, U1.11, U2.1
/SCL1: HEART_SENSOR1.4, Q2.2, R17.2
/SDA: OLED1.4, Q1.3, R4.2, U1.10, U2.32
/SDA1: HEART_SENSOR1.3, Q1.2, R16.2
/TO_FTDI_RX: FTDI.5, PROGRAM_HEADER1.5, U2.31
/TO_FTDI_TX: FTDI.4, PROGRAM_HEADER1.4, U2.30
/TO_RESET: C2.2, R2.2, RESET.3, U2.26
/UPDI: PROGRAM_HEADER1.1, R3.2, U2.27
/VREG_EN: U2.24, U3.3
GND: C1.2, C3.2, C4.2, C5.2, C6.2, C7.2, C8.2, FTDI.1, FTDI.2, HALL_SENSOR1.1, HEART_SENSOR1.1, J6.1, J8.1, OLED1.1, PRIMARY_BATTERY1.2, PROGRAM_HEADER1.6, R9.1, R10.1, RESET.1, RESET.2, RTC_BATT1.2, SW2.1, U1.5, U2.19, U2.29, U3.2, U4.2, microSD.6, microSD.G1, microSD.G2, microSD.G3, microSD.G4
unnamed: 32.768kHz.1, U1.1
unnamed: 32.768kHz.4, U1.2
unnamed: D1.2, R7.2
unnamed: J6.3, R15.2
unnamed: Q3.1, R13.1, U4.3
unnamed: Q3.3, R12.2
unnamed: R11.1, U4.1
VBUS: C1.1, C3.1, C6.1, C7.1, C8.1, D1.1, J1.1, OLED1.2, PRIMARY_BATTERY1.1, PROGRAM_HEADER1.2, Q1.1, Q2.1, Q3.2, R1.1, R2.1, R3.1, R4.1, R5.1, R6.1, R8.1, R13.2, R15.1, U1.14, U2.28, U3.1, microSD.4
VDD: C4.1, C5.1, HALL_SENSOR1.2, HEART_SENSOR1.2, R14.1, R16.1, R17.1, U2.18, U3.5

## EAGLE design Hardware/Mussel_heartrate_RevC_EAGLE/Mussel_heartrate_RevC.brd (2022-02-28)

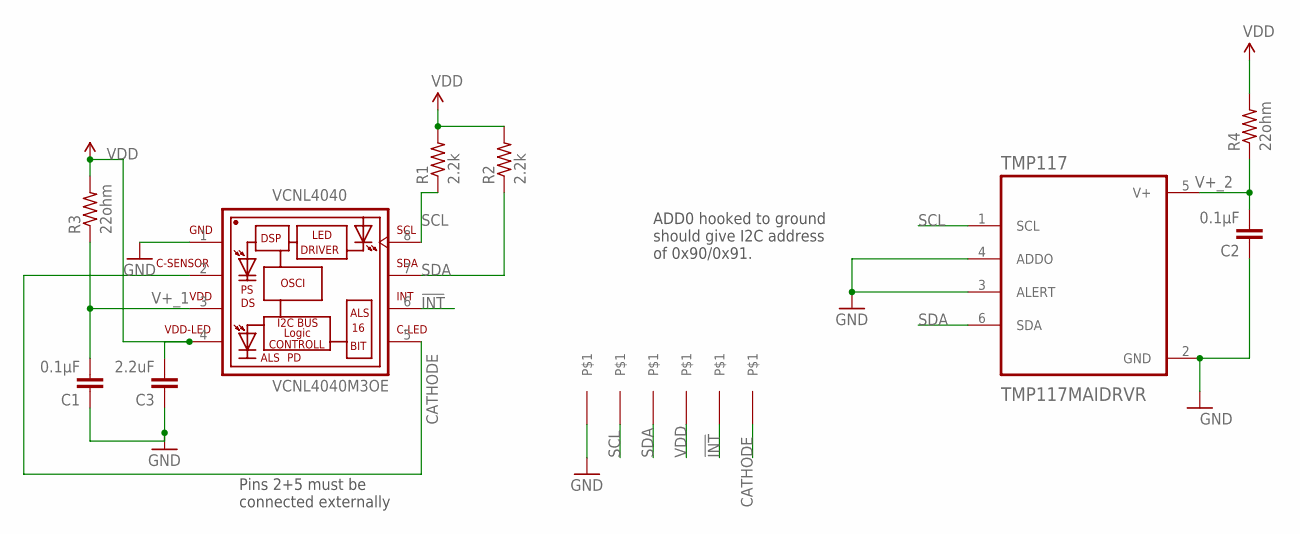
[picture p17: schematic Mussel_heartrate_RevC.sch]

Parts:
!INT, !INT1: PINHD-1X10.7MM_DRILL; 1X01_SMALL_0.7
C1, C2: 0.1µF; C0402
C3: 2.2uF; C0402
GND: PINHD-1X1SMALL; 1X01_SMALL
R1, R2: 2.2k; R0402
R3, R4: 22ohm; R0402
SCL: PINHD-1X1SMALL; 1X01_SMALL
SDA: PINHD-1X1SMALL; 1X01_SMALL
TMP117: TMP117MAIDRVR; SON65P200X200X80-7N
VCNL4040: VCNL4040M3OE; VISHAY_VCNL4040_4X2X1.1
VDD: PINHD-1X1SMALL; 1X01_SMALL

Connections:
!INT: !INT.P$1, VCNL4040.6 (INT)
CATHODE: !INT1.P$1, VCNL4040.2 (C-SENSOR), VCNL4040.5 (C-LED)
GND: C1.1, C2.1, C3.1, GND.1, TMP117.2 (GND), TMP117.3 (ALERT), TMP117.4 (ADDO), VCNL4040.1 (GND)
SCL: R1.1, SCL.1, TMP117.1 (SCL), VCNL4040.8 (SCL)
SDA: R2.1, SDA.1, TMP117.6 (SDA), VCNL4040.7 (SDA)
V+_1: C1.2, R3.1, VCNL4040.3 (VDD)
V+_2: C2.2, R4.1, TMP117.5 (V+)
VDD: C3.2, R1.2, R2.2, R3.2, R4.2, VCNL4040.4 (VDD-LED), VDD.1

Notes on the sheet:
ADD0 hooked to ground should give I2C address of 0x90/0x91.
Pins 2+5 must be connected externally

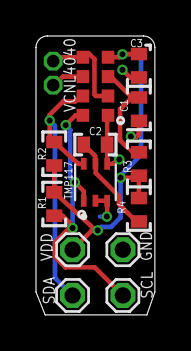
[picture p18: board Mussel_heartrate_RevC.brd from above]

Board: 2 copper layers, 6.6 x 15.5 mm, 15 parts (0 on the bottom side), 8 nets.

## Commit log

2021-10-08 Gerber stuff
    [BivalveBit-B_Cu.gbr, BivalveBit-B_Mask.gbr, BivalveBit-B_Paste.gbr, BivalveBit-B_SilkS.gbr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]
2022-01-19 Example board picture
2022-02-28 Moving hardware files around
    [BivalveBit-B_Cu.gbr, BivalveBit-B_Mask.gbr, BivalveBit-B_Paste.gbr, BivalveBit-B_SilkS.gbr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]
2022-05-18 Saving some layout images
    [BivalveBit.kicad_pcb, BivalveBit.kicad_sch]
2022-06-08 Transferring design to KiCad
    [BivalveBit.kicad_pcb, Hall_effect_sensor_A139x.kicad_sch, Hall_effect_sensor_board_A139x.kicad_pcb, Hall_effect_sensor_board_A139x.kicad_sch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]
2023-01-19 Thickening traces, no layout changes
    [BivalveBit.kicad_pcb, BivalveBit.kicad_sch]
2023-07-13 Re-saving in KiCad 7
    [BivalveBit.kicad_pcb, BivalveBit.kicad_sch]
2024-03-04 Creating Rev F
    Added mounting holes, thickened traces
    [BivalveBit_RevE_BOM.xlsx, BivalveBit_RevF.kicad_pcb, BivalveBit_RevF.kicad_sch, BivalveBit_RevF.sch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]
2024-03-04 Few minor label changes
    [BivalveBit_RevF.kicad_pcb]
2025-05-29 Moving images around
    [BivalveBit_RevF_BOM.xlsx]
2025-05-29 Moving parts list here
    [BivalveBit_parts_list.xlsx]
